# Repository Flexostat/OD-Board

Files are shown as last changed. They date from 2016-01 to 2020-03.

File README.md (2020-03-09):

# OD-Board
This repository contains the optical density measurement PCB and firmware source
 and production files for the Flexostat and syphonstat.

### Production_files/PCB/
These are the files that get zipped and sent to the PCB fabricator.

### Production_files/firmware.hex
This is the firmware file to be loaded onto the OD board.  

### seeed_bom.csv
This is the BOM file used by Seeedstudio to assemble the PCB.  If assembled by
Seeedstudio, the light sensors still need to be added afterwards since seeed
does not stock them.

<br />This work is licensed under a <a rel="license" href="http://creativecommons.org/licenses/by/4.0/">Creative Commons Attribution 4.0 International License</a>.

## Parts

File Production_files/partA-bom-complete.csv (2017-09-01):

Part/Designator | Manufacture Part Number | Quantity | notes
C1 | CC0805KKX7R8BB105 | 1 | may substitute for any similar capacitor
C2 | TAJC476K016RNJ | 1 | may substitute for any similar capacitor
ISP J5 | P125-12A1BS116A1 | 2 | 2x3 0.1" header, male
J1 | 54602-908LF | 1
J3 | P125-1104A0BS116A1 | 1 | 4pin 0.1" header, male, on back side
J4 | P125-1103A1BS116A1 | 1 | 3pin 0.1" header, male
Q3 Q4 | CJ2302 | 2
R3 | RC0603JR-074K7L | 1 | may substitute for any similar resistor
U1 | ATMEGA328P-AU | 1
J6 J7 | F185-1108A1BSYC1 | 2 | 8pin 0.1" header, female
LF1 LF2 | TSL235R-LF | 2 | on back side

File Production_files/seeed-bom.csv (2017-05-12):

Part/Designator | Manufacture Part Number/Seeed SKU | Quantity
C1 | CC0805KKX7R8BB105 | 1
C2 | TAJC476K016RNJ | 1
ISP, J5 | P125-12A1BS116A1 | 2
J1 | MJ88-BX11-RVSL2 | 1
J3 | P125-1104A0BS116A1 | 1
J4 | 320020079 | 1
Q3, Q4 | CJ2302 | 2
R3 | RC0603JR-074K7L | 1
U1 | ATMEGA328P-AU | 1
J6,J7 | F185-1108A1BSYC1 | 1

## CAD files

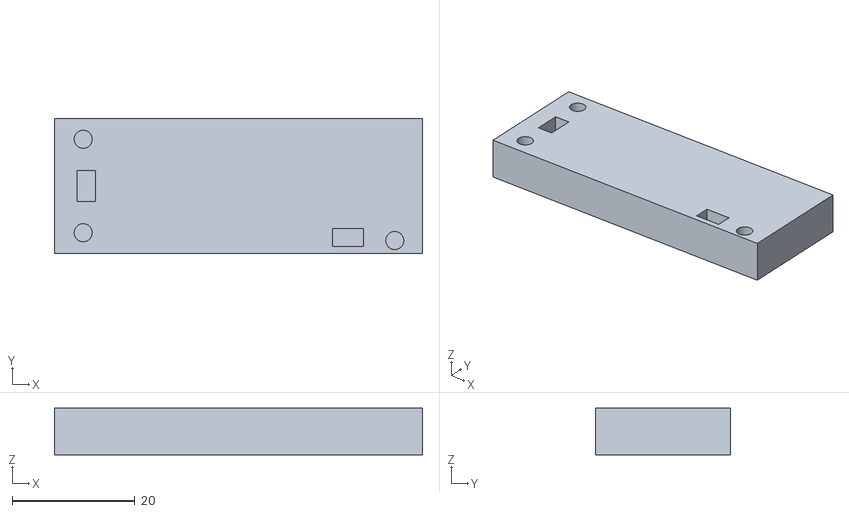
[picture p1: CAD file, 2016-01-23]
Production_files/PCB_assembly_jig.stl
60.0 x 22.0 x 7.60

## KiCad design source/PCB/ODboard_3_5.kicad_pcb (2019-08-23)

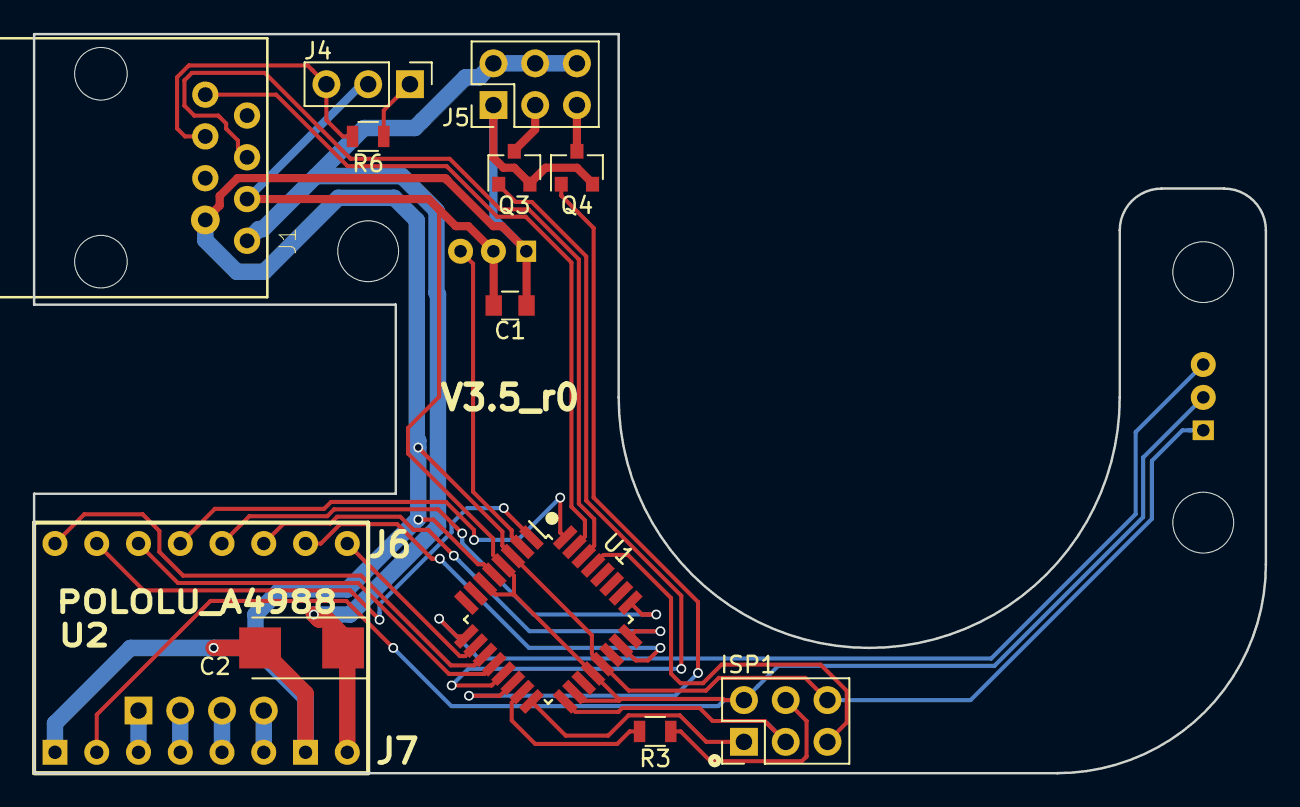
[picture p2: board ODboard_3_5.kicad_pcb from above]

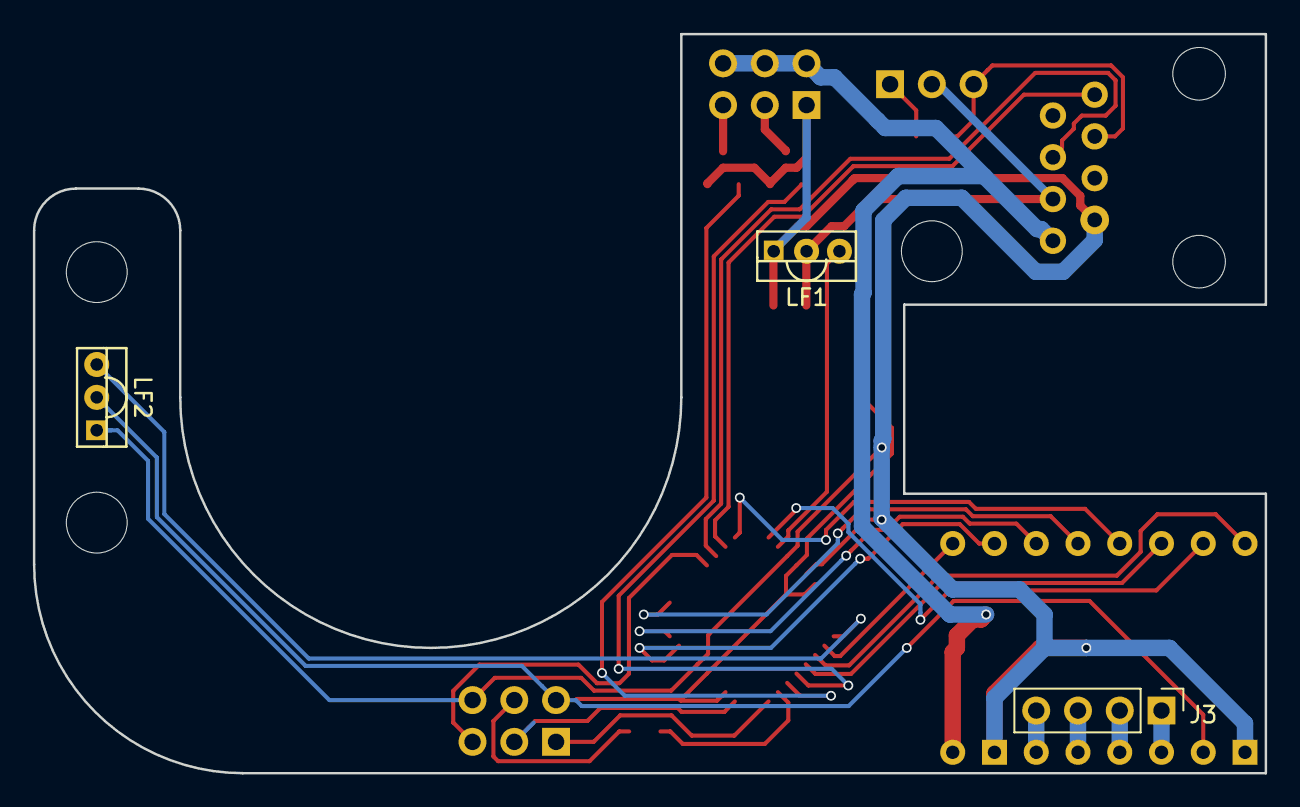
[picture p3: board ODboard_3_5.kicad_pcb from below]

Board: 2 copper layers, 74.9 x 45.0 mm, 15 parts (3 on the bottom side), 30 nets.

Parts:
C1: 1uF; C_0805
C2: 47uF; CP_Tantalum_Case-C_EIA-6032-28_Reflow
ISP1: AVR-ISP-6; Pin_Header_Straight_2x03_Pitch2.54mm
J1: RJ45; 54602-908LF
J3: CONN_01X04; Pin_Header_Straight_1x04_Pitch2.54mm
J4: CONN_01X03; Pin_Header_Straight_1x03_Pitch2.54mm
J5: CONN_02X03; Pin_Header_Straight_2x03_Pitch2.54mm
LF1, LF2: TSL235R-LF; TSL235R-LF-S
Q3, Q4: CJ2302; SOT-23
R3, R6: 10k; R_0805
U1: ATMEGA328P-A; TQFP-32_7x7mm_Pitch0.8mm
U2: POLOLU_A4988; SWDIP8_.6W

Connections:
+5V: C1.1, ISP1.2, J1.6, J4.2, LF1.2, LF2.2, U1.4, U1.6, U1.18, U1.20, U2.2
+12V: C2.1, J1.8, J5.2, J5.4, J5.6, U2.8
/LF1: LF1.3, U1.2
/LF2: LF2.3, U1.9
/M!EN: U1.10, U2.9
/M!RST: U1.32, U2.13
/M!SLP: U1.12, U2.14
/MDIR: U1.11, U2.16
/MISO: ISP1.1, U1.16
/MS1: U1.23, U2.10
/MS2: U1.24, U2.11
/MS3: U1.25, U2.12
/OC2A: R3.2, U1.15
/OC2B: U1.1, U2.15
/PB1: Q3.1, U1.13
/PB2: Q4.1, U1.14
/SCK: ISP1.3, U1.17
/S_RX: J1.4, U1.30
/S_TX: J1.1, U1.31
/rst: ISP1.5, U1.29
GND: C1.2, C2.2, ISP1.6, J1.7, J5.1, LF1.1, LF2.1, Q3.2, Q4.2, U1.3, U1.5, U1.21, U2.1, U2.7
unnamed: ISP1.4, R3.1
unnamed: J1.3, J4.3, R6.2
unnamed: J3.1, U2.3
unnamed: J3.2, U2.4
unnamed: J3.3, U2.5
unnamed: J3.4, U2.6
unnamed: J4.1, R6.1
unnamed: J5.3, Q3.3
unnamed: J5.5, Q4.3

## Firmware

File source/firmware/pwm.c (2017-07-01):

/*
 * pwm.c
 *
 * Created: 8/2/2011 3:10:29 PM
 *  Author: soslab
 */ 
#include "pwm.h"
#include "EEMAP.h"
#include <avr/io.h>
#include <avr/interrupt.h>
#include <avr/eeprom.h>

volatile uint16_t millist;
volatile uint16_t ust;
volatile uint16_t us_p_int;

//setup stir motor PWM
//TODO: convert this to work with timer2
void pwm_init() {
	/******STIR INIT*******/

	DDRD |= 0x08; //PD3:OSC2B output
	DDRD |= 0x04; //PD2 -> !MRST
	DDRD |= 0x40; //PD6 -> !MEN
	DDRD |= 0x80; //PD7 -> MDIR
	DDRB |= 0x01; //PB0 -> !MSLP
	DDRC |= 0x07; //PC0-PC2 output  -> MS1-MS3
	/************************************************************************/
	/*
	MS1 	MS2 	MS3 	Microstep Resolution
	Low 	Low 	Low 	Full step
	High	Low 	Low 	Half step
	Low 	High	Low 	Quarter step
	High	High	Low 	Eighth step
	High	High	High	Sixteenth step                                  */
	/************************************************************************/
	uint8_t stepmode = eeprom_read_byte(EE_ADDR_STEP);
	stepmode = stepmode == 0xff ? 0 : stepmode &0x07;  //take default full steps, mask lower 3 bits
	PORTC &= ~0x07; //PC0-PC2 low = full step
	PORTC |= stepmode;
	//PORTC |= 0x01; //half step
	PORTD |= 0x04; //pull motor reset high
	PORTD &= ~0x40; //pull motor enable low
	PORTB |= 0x01; //pull motor sleep high
	
	
	//CTC mode, toggle on compare match  B
	TCCR2A = 0x02 | 0x10; 
	//cksel /256,
	TCCR2B = 0x06;
	
	//toggle on counter top/2  
	//OCR2A = COUNTER_TOP/2;
	uint8_t ctop = eeprom_read_byte(EE_ADDR_COUNT);
	ctop = (ctop>32 && ctop<=64) ? ctop : COUNTER_TOP;
	OCR2A = ctop;
	us_p_int = (COUNTER_TOP+1)*(256/8);
	OCR2B = 0;
	
	TIMSK2 = 1<<OCIE2A; 
	
}

//one epoch is 2/STIR_SPEED seconds
//takes roughly 120 cycles every US_PER_INT
ISR (TIMER2_COMPA_vect) { 
  ust += us_p_int;
  while (ust>1000) {
	  ust-=1000;
	  millist +=1;
  }
}

uint16_t millis() {
  return millist;
}

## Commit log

2014-03-18 added eagle files for LED board. version 3.1
    [page1.brd, page1.sch]
2014-03-18 updated to version 3.2 of led PCB
    [page1.brd, page1.sch]
2014-03-19 added BOM file for ordering LED board from seeed studio preassembled
    [seeed_BOM_File.csv]
2014-04-04 added support for LED board version 3.2
2014-04-04 Updated PCB design for ledboard 3.2r1
    [page1.GBL, page1.GBO, page1.GBP, page1.GBS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]
2014-05-13 reorg directory structure
    [page1.GBL, page1.GBO, page1.GBP, page1.GBS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]
2014-05-13 more file reorg
    [page1.GBL, page1.GBO, page1.GBP, page1.GBS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]
2014-05-13 updated c code to reflect new boards. included hex file
2014-08-07 LED board update rev3. Vs and Vss corrected
    [page1.GBL, page1.GTL, page1.GTO, page1.brd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]
2014-12-19 millis now counts the full range of uint16_t.
2014-12-19 now pulls enable pin high for stirring on newest board rev
2015-08-12 added control over stirrer driver OE
    [page1.GBL, page1.GTL, page1.GTO, page1.brd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]
2015-08-12 updated bom file for seeed's new format
    [seeed_BOM_File.csv]
2015-08-28 fixed bom to align with seeed's new partnumber
    [seeed_BOM_File.csv]
2015-09-08 soldering jig
    [PCB_assembly_jig.stl]
2015-09-30 fixed partnumber changed by seeed
    [seeed_BOM_File.csv]
2016-01-23 file structre reorg
    [PCB_assembly_jig.stl, page1.GBL, page1.GBO, page1.GBP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]
2016-01-23 updated PCB
    [page1.GBL, page1.GBO, page1.GBP, page1.GBS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]
2016-01-23 forgot this in the last push
    [seeed-bom.csv]
2016-01-23 updated code to match PCB 3.3
2016-02-11 updated footprint for rj45
    [page1.GBL, page1.GBO, page1.GBP, page1.GBS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]
2017-05-12 updated pcb with better motor drivers -- tested and working.
    [page1.GBL, page1.GBO, page1.GBS, page1.GTL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]
2017-07-01 updated BOM.
    [seeed-bom-OPL.csv, seeed-bom-complete.csv]
2017-08-22 Redesign from scratch. in KiCAD new design should be easier to assemble and leaves room for better laser alignment
    [ODboard_3_5-B.Cu.gbl, ODboard_3_5-B.Mask.gbs, ODboard_3_5-B.SilkS.gbo, ODboard_3_5-Edge.Cuts.gm1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]
2017-09-01 BOM had M instead of F pin headers for stepper driver
    [partA-bom-complete.csv, partA-bom-seeed-only.csv]
2019-08-23 update to kicad 5
    [ODboard_3_5.kicad_pcb, ODboard_3_5.sch]
